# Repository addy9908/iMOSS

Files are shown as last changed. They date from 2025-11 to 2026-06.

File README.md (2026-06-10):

# <b>iMOSS</b>: Immobility/Mobility Optimized Scoring System
<p align="center">
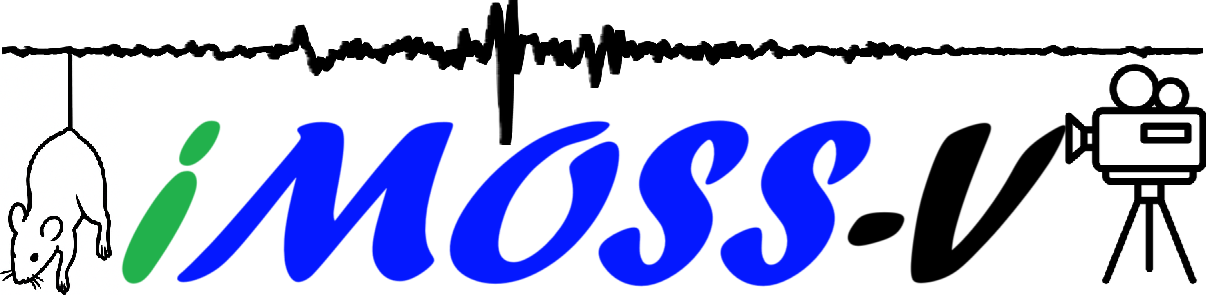
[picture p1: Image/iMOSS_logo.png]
iMOSS Logo
  
</p>   

<p align="center">
  <a href="https://www.frontiersin.org/journals/behavioral-neuroscience/articles/10.3389/fnbeh.2026.1819512/full">
    
  </a>
  
  
  
</p>

---

## 📌 Overview

**iMOSS** is an open-source platform for high-resolution immobility scoring in the tail suspension test (TST). By enabling precise synchronization with neural recordings, this platform supports critical advances in neuroscience and public health research.

### 🔑 Key Features
| Feature | Description |
|---|---|
| **iMOSS-MV** | Frame-accurate binary behavior manual scoring |
| **iMOSS-AS** | High-frequency automated scoring (80 Hz) |
| **Integration** | Seamless synchronization with neural recording systems |
| **Analysis** | Standardized and reproducible behavioral data processing |

---

## 🔄 Workflow

<p align="center">
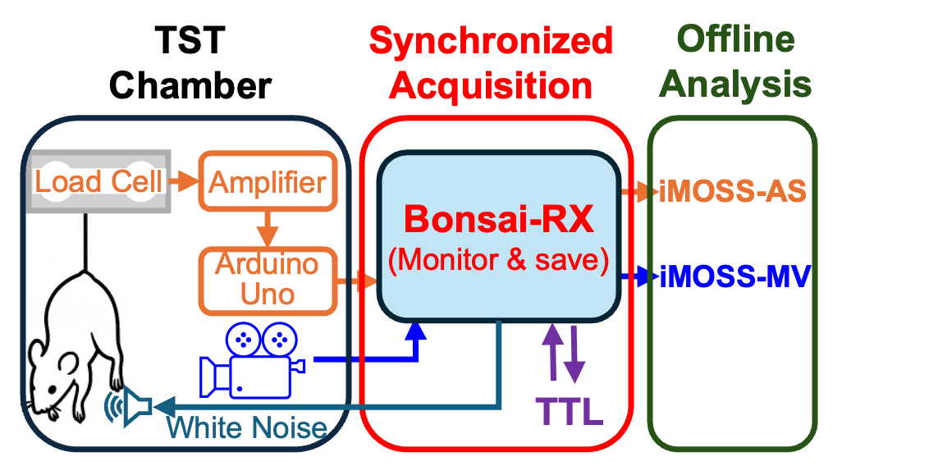
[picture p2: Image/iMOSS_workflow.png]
Detailed Workflow
  
</p>

---

## 🧰 Materials

<p align="center">
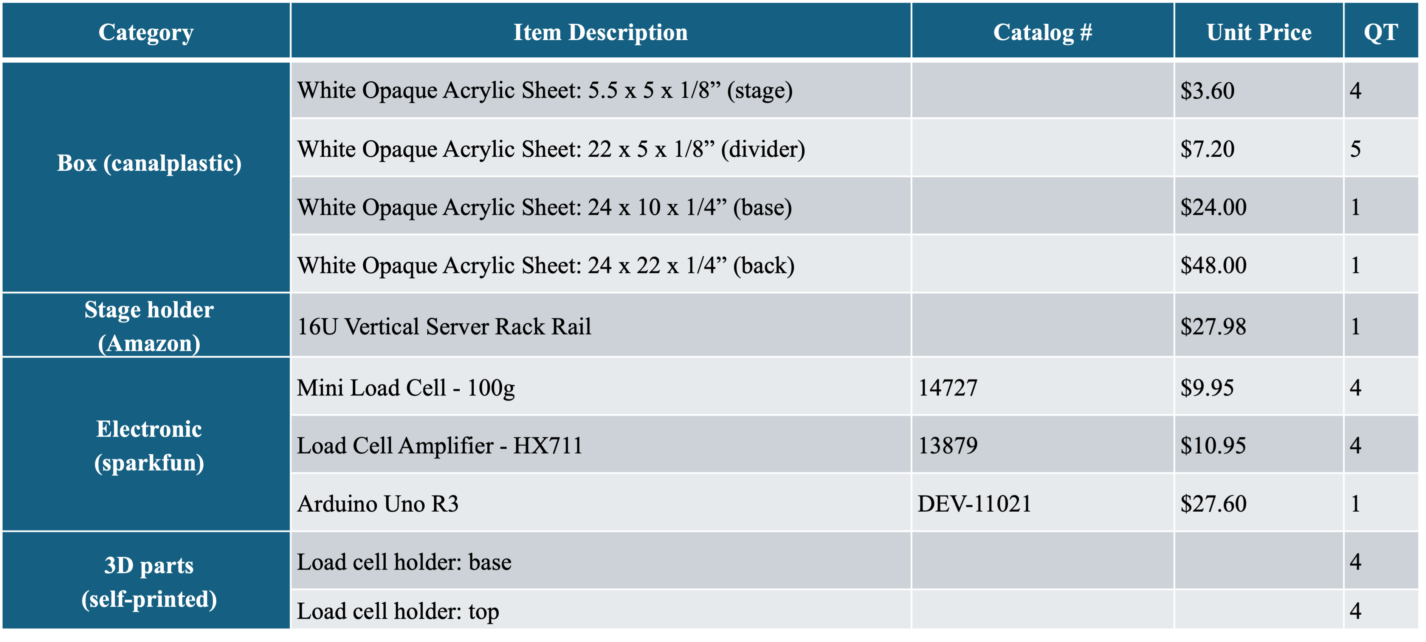
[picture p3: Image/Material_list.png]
Material List
  
</p>

---

## 🏗️ TST Chamber Design

<p align="center">
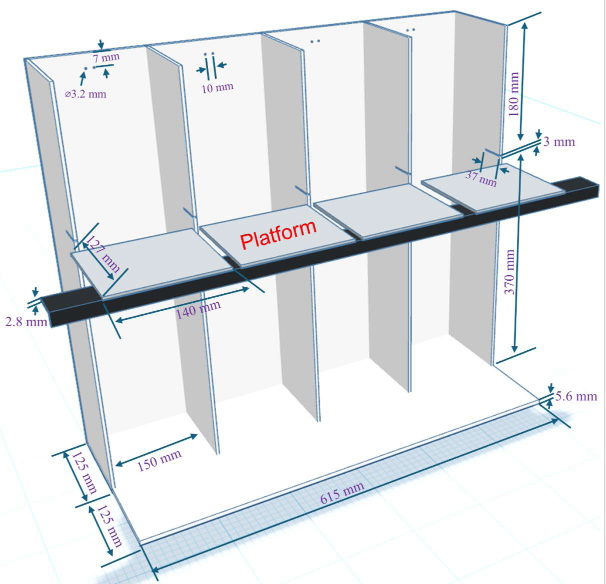
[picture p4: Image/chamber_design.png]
Chamber Design
	
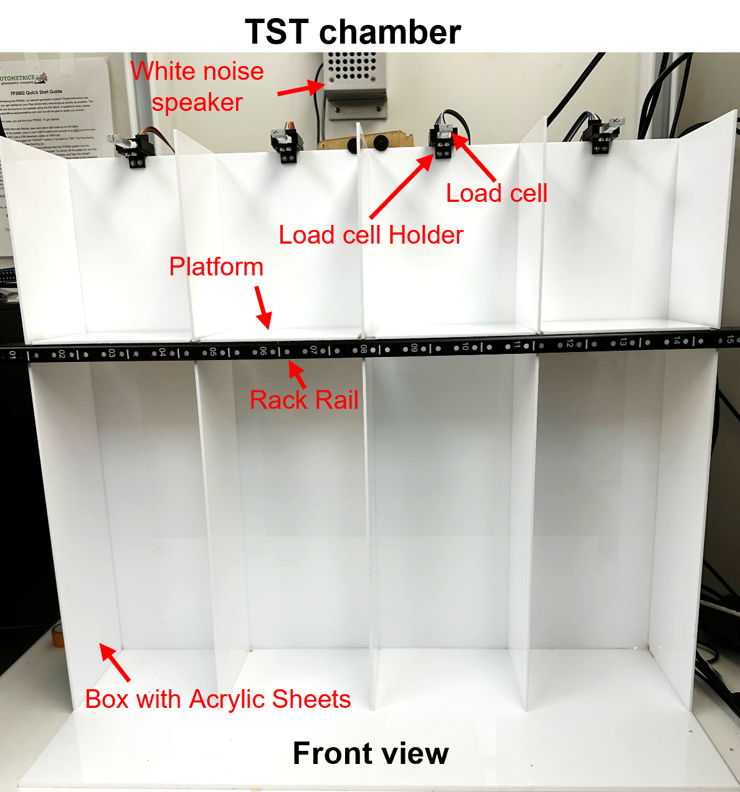
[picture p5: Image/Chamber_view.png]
Front View
	 
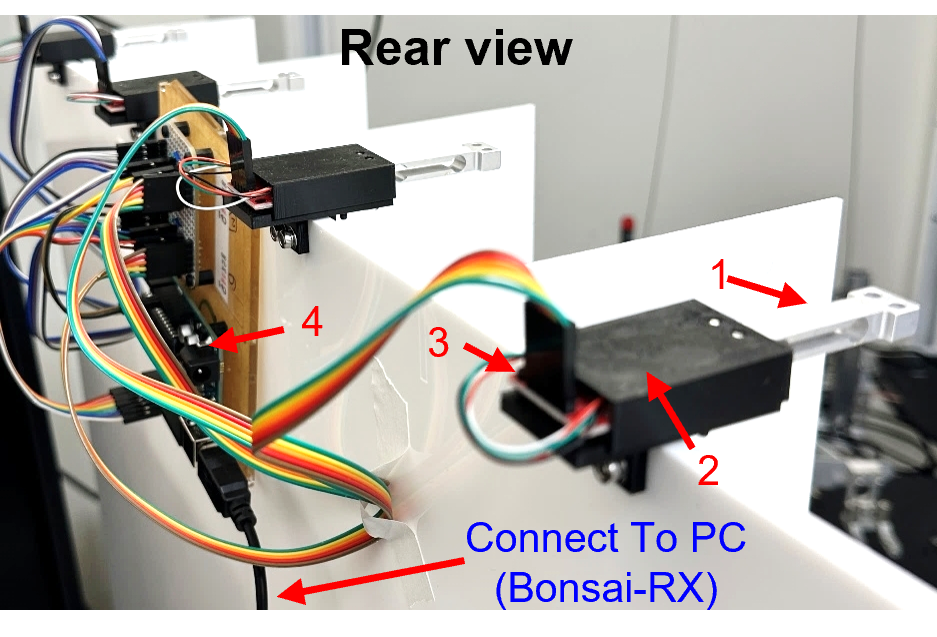
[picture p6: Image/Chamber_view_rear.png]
Rear View
	 
</p>

---

## ⚙️ iMOSS-AS Hardware Module

### 🔌 Design & Wiring

<p align="center">
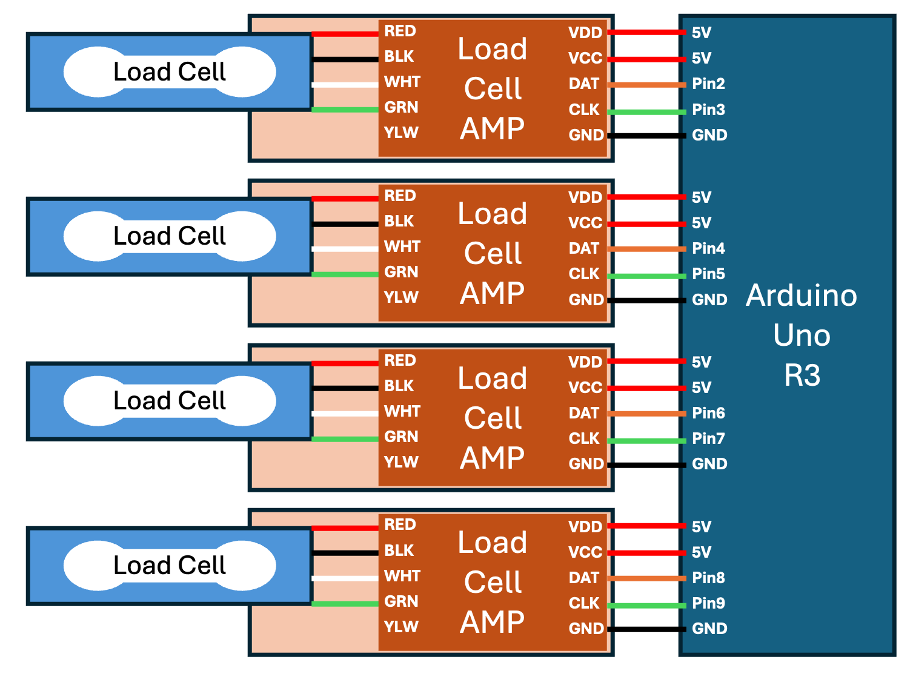
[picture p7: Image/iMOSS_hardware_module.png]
Hardware Wiring
  
</p>

### ⚠️ Important Note

To achieve the **80 Hz sampling rate**, the load cell amplifier must be modified as shown below:

<p align="center">
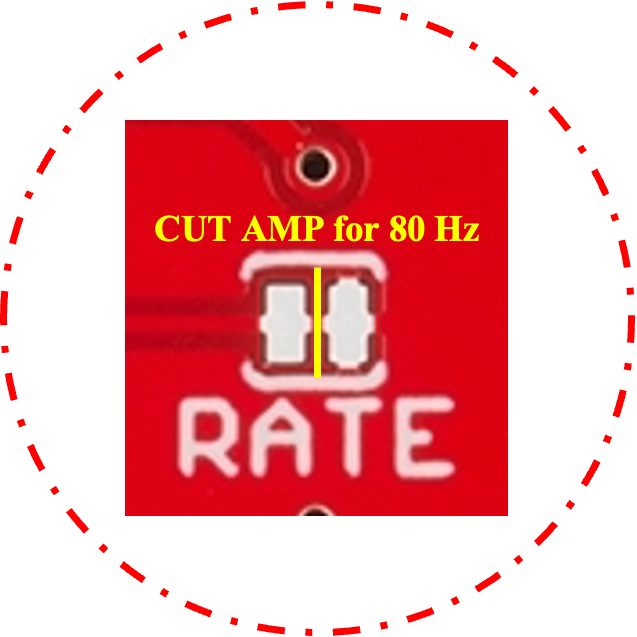
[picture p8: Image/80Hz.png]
Loadcell Amplifier Modification
  
</p>

---

## 🔌 Firmware (Arduino Uno)

### 📥 Download
The firmware file is available here: `Firmware/iMOSS_AS_V1.ino`  
[Direct Link to Firmware Folder](https://github.com/addy9908/iMOSS/tree/main/Firmware)

### 🚀 Flashing Instructions
1. Install **Arduino IDE**.
2. Connect your **Arduino Uno**.
3. Open `iMOSS_AS_V1.ino`.
4. Click **Upload**.

<details>
<summary>Click for Arduino Code Preview</summary>

```cpp
//-------------------------------------------------------------------------------------
// iMOSS-AS for automatic tail suspension test with 4 load cells
//Author: Zengyou Ye at NIDA/IRP
//Date: 10/23/2024

// Settling time (number of samples) and data filtering can be adjusted in the config.h file of HX711_ADC.h
// HX711-ADC from: https://github.com/olkal/HX711_ADC
//---------------------------------

#include <HX711_ADC.h>

//pins:
const int HX711_dout_1 = 2; //mcu > HX711 no 1 dout pin
const int HX711_sck_1 = 3; //mcu > HX711 no 1 sck pin
const int HX711_dout_2 = 4; //mcu > HX711 no 2 dout pin
const int HX711_sck_2 = 5; //mcu > HX711 no 2 sck pin
const int HX711_dout_3 = 6; //mcu > HX711 no 3 dout pin
const int HX711_sck_3 = 7; //mcu > HX711 no 3 sck pin
const int HX711_dout_4 = 8; //mcu > HX711 no 4 dout pin
const int HX711_sck_4 = 9; //mcu > HX711 no 4 sck pin

//HX711 constructor (dout pin, sck pin)
HX711_ADC LoadCell_1(HX711_dout_1, HX711_sck_1); //HX711 1
HX711_ADC LoadCell_2(HX711_dout_2, HX711_sck_2); //HX711 2
HX711_ADC LoadCell_3(HX711_dout_3, HX711_sck_3); //HX711 3
HX711_ADC LoadCell_4(HX711_dout_4, HX711_sck_4); //HX711 4

unsigned long t = 0;
const int serialPrintInterval = 12.5; //80Hz to match 80SPS
static boolean togo = 0;

void setup() {
  Serial.begin(57600);
  delay(10);
  Serial.println();
  Serial.println("Starting...");

  float calibrationValue_1; // calibration value load cell 1
  float calibrationValue_2; // calibration value load cell 2
  float calibrationValue_3; // calibration value load cell 3
  float calibrationValue_4; // calibration value load cell 4

  calibrationValue_1 = 13.3; // uncomment this if you want to set this value in the sketch
  calibrationValue_2 = 13.3; // uncomment this if you want to set this value in the sketch
  calibrationValue_3 = 13.3; // uncomment this if you want to set this value in the sketch
  calibrationValue_4 = 13.3; // uncomment this if you want to set this value in the sketch

  LoadCell_1.begin();
  LoadCell_2.begin();
  LoadCell_3.begin();
  LoadCell_4.begin();

  unsigned long stabilizingtime = 2000; // tare preciscion can be improved by adding a few seconds of stabilizing time
  boolean _tare = true; //set this to false if you don't want tare to be performed in the next step
  byte loadcell_1_rdy = 0;
  byte loadcell_2_rdy = 0;
  byte loadcell_3_rdy = 0;
  byte loadcell_4_rdy = 0;

  while ((loadcell_1_rdy + loadcell_2_rdy + loadcell_3_rdy + loadcell_4_rdy) < 4) { //run startup, stabilization and tare, both modules simultaniously
    if (!loadcell_1_rdy) loadcell_1_rdy = LoadCell_1.startMultiple(stabilizingtime, _tare);
    if (!loadcell_2_rdy) loadcell_2_rdy = LoadCell_2.startMultiple(stabilizingtime, _tare);
    if (!loadcell_3_rdy) loadcell_3_rdy = LoadCell_3.startMultiple(stabilizingtime, _tare);
    if (!loadcell_4_rdy) loadcell_4_rdy = LoadCell_4.startMultiple(stabilizingtime, _tare);
  }
  if (LoadCell_1.getTareTimeoutFlag()) {
    Serial.println("Timeout, check MCU>HX711 no.1 wiring and pin designations");
  }
  if (LoadCell_2.getTareTimeoutFlag()) {
    Serial.println("Timeout, check MCU>HX711 no.2 wiring and pin designations");
  }
  if (LoadCell_3.getTareTimeoutFlag()) {
    Serial.println("Timeout, check MCU>HX711 no.3 wiring and pin designations");
  }
  if (LoadCell_4.getTareTimeoutFlag()) {
    Serial.println("Timeout, check MCU>HX711 no.4 wiring and pin designations");
  }
  LoadCell_1.setCalFactor(calibrationValue_1); // user set calibration value (float)
  LoadCell_2.setCalFactor(calibrationValue_2); // user set calibration value (float)
  LoadCell_3.setCalFactor(calibrationValue_3); // user set calibration value (float)
  LoadCell_4.setCalFactor(calibrationValue_4); // user set calibration value (float)
  Serial.print("HX711 measured sampling rate Hz: ");
  Serial.println(LoadCell_1.getSPS());
  Serial.println("Startup is complete");
}

void loop() {
  while (togo==0){
    char inByte = Serial.read();
    if (inByte == 'g') {
      togo=1;
      //Serial.println("ms,lc1,lc2,lc3,lc4");
      //Serial.println("experiments on");
    }
    if (inByte == 't') {
      LoadCell_1.tareNoDelay();
      LoadCell_2.tareNoDelay();
      LoadCell_3.tareNoDelay();
      LoadCell_4.tareNoDelay();
      delay(5000);
    }    
  }
  if(togo){
    LoadCell_1.update();
    LoadCell_2.update();
    LoadCell_3.update();
    LoadCell_4.update();

    if (millis() >= t + serialPrintInterval) {
      t = millis();
      float a = LoadCell_1.getData();
      float b = LoadCell_2.getData();
      float c = LoadCell_3.getData();
      float d = LoadCell_4.getData();
      
      Serial.print(t);
      Serial.print(",");
      Serial.print(a);
      Serial.print(",");
      Serial.print(b);
      Serial.print(",");
      Serial.print(c);
      Serial.print(",");
      Serial.println(d);
    }
  }
  if (Serial.read() == 'q') {
    togo=0;
  }
}
```
</details>

---

## 📡 Data Acquisition (Bonsai-RX)

### 📥 Workflow File
`Bonsai/ZY_tailSuspension_V11_Opstim.bonsai`
`Bonsai/ZY_TST_FP.bonsai`

### 💻 Workflow Layout and UI from V11
<p align="center"> 
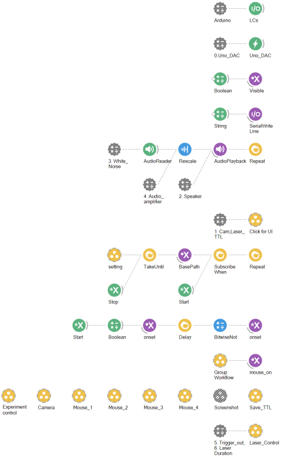
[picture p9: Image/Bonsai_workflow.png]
Bonsai Layout
	
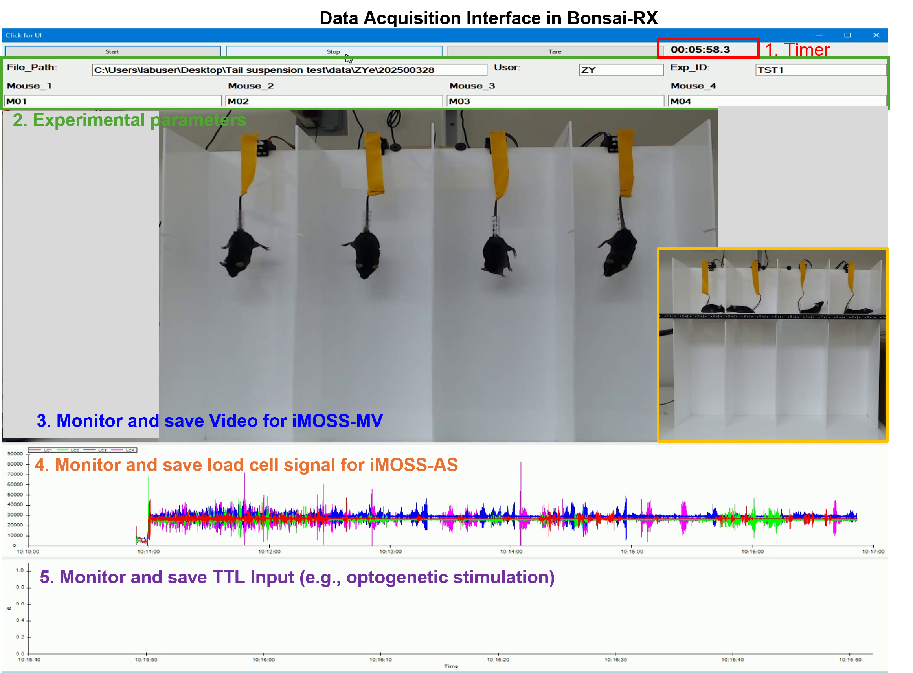
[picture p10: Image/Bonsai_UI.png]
Bonsai UI
	
</p>

---

## 🧪 Data Analysis

### Python Envirement Installation:
  1. Install Anaconda
  2. Importing the listed "[yaml](Data_Analysis/)" environment file 
  3. Install Spyder in this environment
  4. Download Main script as well as Required script in the same folder
  4. Run Main Script inside Spyder.
---
### 🖥️ iMOSS-MV (Manual Scoring)
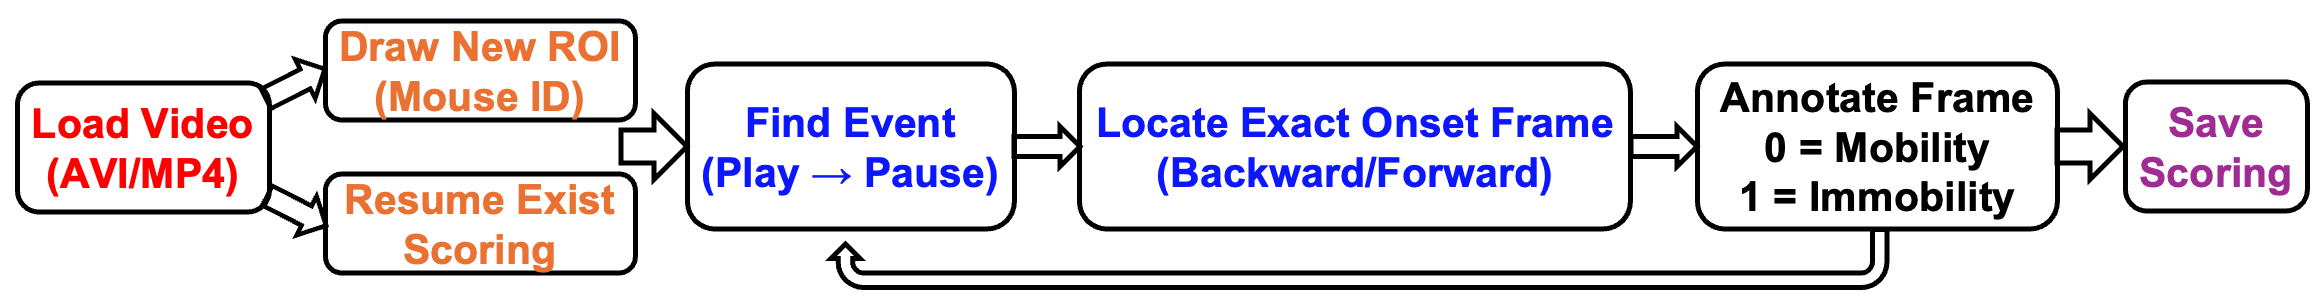
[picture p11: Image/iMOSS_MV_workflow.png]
iMOSS-MV Workflow


#### 📦 Requirements
| Main Script | Conda Env | Link to Folder | Spyder Version |
|---|---|---|---|
| zy_iMOSS_MV_20251119.py | video_scorer.yaml | [iMOSS-MV V1](Data_analysis/iMOSS_MV/V1) | 6.05 |
| zy_iMOSS_MV_withDuration.py | video_scorer.yaml | [iMOSS-MV V2](Data_analysis/iMOSS_MV/V2) | 6.05 |
| zy_iMOSS_MV_20260501.py | iMOSS_MV_20260501.yml | [iMOSS-MV V3](Data_analysis/iMOSS_MV/V3) | 6.13 |

<p align="center"> iMOSS MV V1
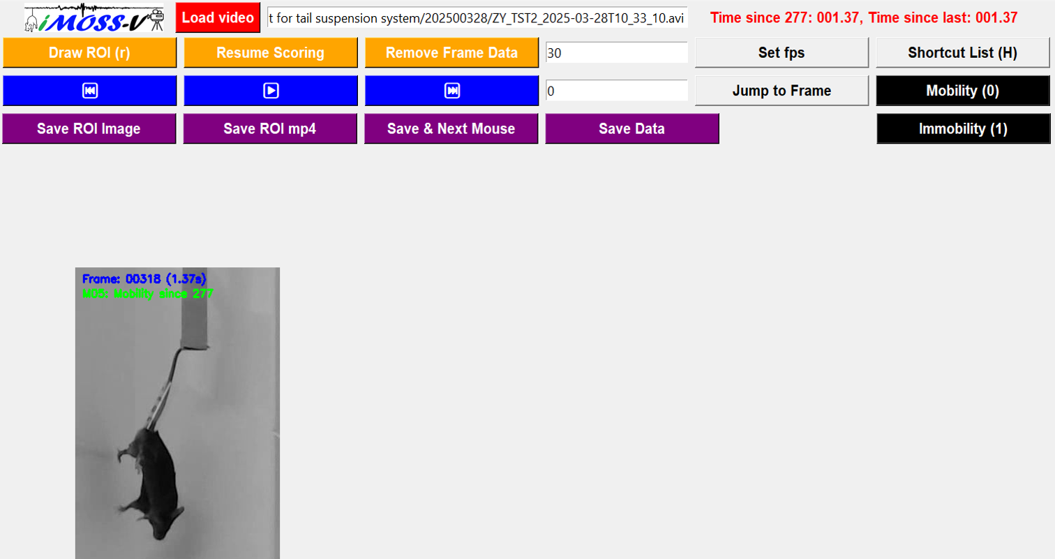
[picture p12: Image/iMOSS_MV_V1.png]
iMOSS MV V1
	
</p>
<p align="center"> iMOSS MV V3
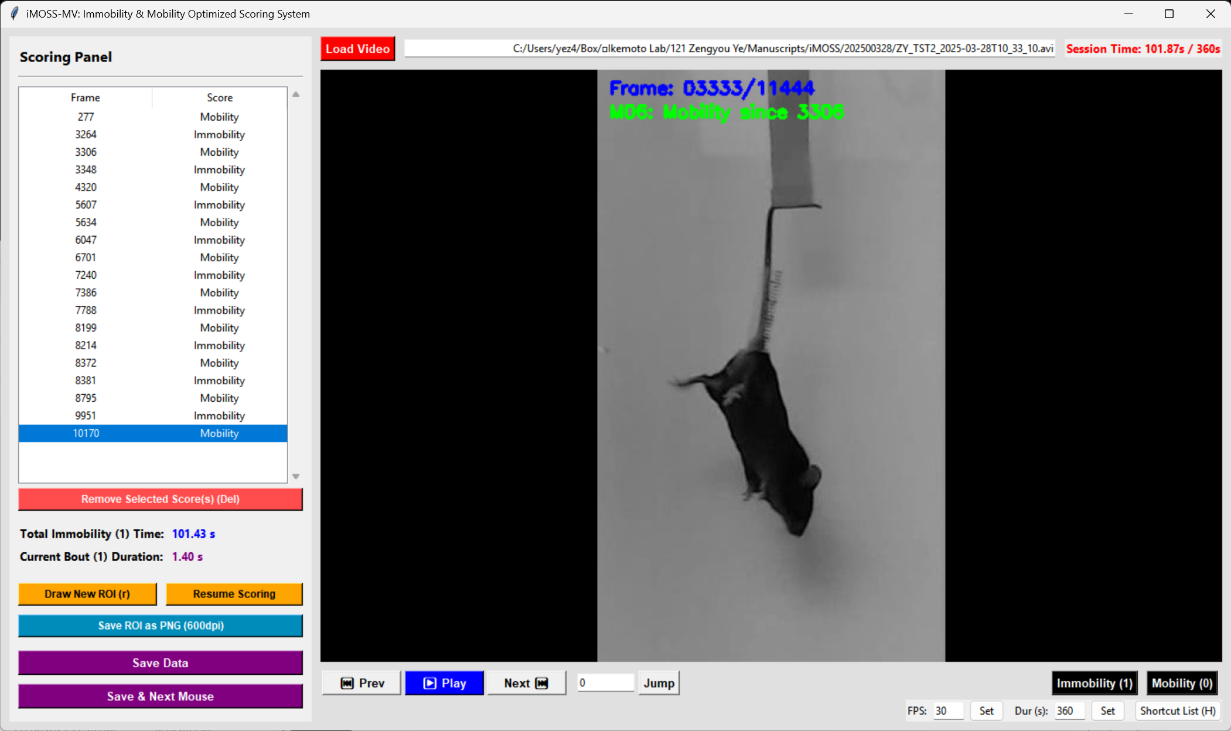
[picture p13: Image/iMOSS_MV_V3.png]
iMOSS MV V3
	
</p>

### Scoring with iMOSS-MV (zy_iMOSS_MV_20251119.py):
  1. Load video file
  2. Draw ROI, and comforn the ROI with SPACE or ENTER key, then define Mouse_ID
  3. Use Buttons or keyboard shrcuts (detailed in "shortcuts" bottun) to navigate the video and mark the events.
  4. When finish annotating a ROI, click "Save Data" to save the ROI information (csv file) and immobility data (excel file)
  5. Optional:
     1. click "Save & Next Mouse" will also save the data and promp user to choose next ROI
     2. click "Draw ROI (r)" will also prompt user to save the data if exist.

⚠️ update: 
* [**V2**](Data_Analysis/iMOSS_MV/V2): allow user to set the duration of session and adjust the size of video for other purposes.
* [**V3**](Data_Analysis/iMOSS_MV/V2): new design with better layout, and improve the Compatibility with new opencv  
---

### 🤖 iMOSS-AS (Automated Scoring)

<p align="center"> iMOSS-AS Workflow </p>

#### 📦 Requirements
| Main Script | Required Script | Conda Env | Folder | Spyder Version |
|---|---|---|---|---|
| zy_iMOSS_AS_20251119_clean.py| zy_importer_lite_V4.py; zy_preset_mpl_v2.py | zy_NIDA_20240905.yaml | [iMOSS-AS V1](Data_analysis/iMOSS_AS/Archive_V1) | 6.05 |
| zy_iMOSS_AS_20260501_with_summary.py | zy_importer_lite_V5.py; zy_preset_mpl_v2.py | iMOSS_AS.yml| [iMOSS-AS V2](Data_analysis/iMOSS_AS/V2) | 6.13 |

---

## 📄 Publication

For detailed scientific methodology, validation, and synchronization with Fiber Photometric recording, please refer to our paper:  
[Frontiers in Behavioral Neuroscience (2026)](https://www.frontiersin.org/journals/behavioral-neuroscience/articles/10.3389/fnbeh.2026.1819512/full)

---

## 📚 Citation

```bibtex
@article{iMOSS2026,
  title={iMOSS: an integrated open-source tail suspension test platform for high-resolution immobility scoring and synchronization with neural activity},
  journal={Frontiers in Behavioral Neuroscience},
  year={2026},
  doi={10.3389/fnbeh.2026.1819512}
}
```

---

## 🤝 Contributions

We welcome feedback and contributions from the community. If you find this platform helpful for your research, please ⭐ the repository.

## This iMOSS platform is under a MIT license.

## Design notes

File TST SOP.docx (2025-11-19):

Tail Suspension Test Standard Operating Protocol

Zengyou Ye at Ikemoto Lab, NIDA

1. Open Bonsai:
  - Select the appropriate program: ZY_tailSuspension_V8_Opstim.
2. Confirm Hardware Selections in Bonsai:
  - Verify the Arduino Uno port, camera, and speaker settings on the right panel.
3. Optional - Optogenetic Stimulation Setup:
  a. Power on the Doric "Laser Diode Fiber Light Source" and launch the corresponding software.
  b. Within the software, connect the "Laser Diode Fiber Light Source".
  c. Load an existing configuration or create a new one (gate control with restart option is recommended).
  d. Confirm the current output and start the setup, then leave it running.
4. Run Bonsai File:
  - This will initiate white noise playback and display a User Interface (UI). If the UI does not appear automatically, click the "Click for UI" node.
5. Set Parameters in UI:
  - Enter the file path, User ID, Experimental ID, and Mouse ID in the UI.
6. Start the Test:
  a. Click the "Start" button.
  b. Place the mice onto the stage of the Tail Suspension Test (TST) box.
  c. For Optogenetic Stimulation: Place the mice first, connect the fiber patch cable to the cannulas, then click "Start"
7. Begin Recording:
  - Remove the stage from the TST box to initiate recording and monitor the timer on the UI.
8. End Recording:
  - After 6 minutes, replace the stage in the TST box and click the "Stop" button.
9. Remove Mice:
  - Take the mice off the stage.
10. Repeat for Additional Mice:
  - Repeat steps 5-9 for the next set of mice.

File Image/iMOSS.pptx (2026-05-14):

## Hardware of iMOSS

Zengyou Ye
https://www.github.com/addy9908/iMOSS
Updated on 05/13/2026

## iMOSS workflow

TST
Chamber

White Noise

Synchronized
Acquisition

Bonsai-RX
(Monitor & save)

Offline
Analysis

iMOSS-AS

iMOSS-MV

Load Cell

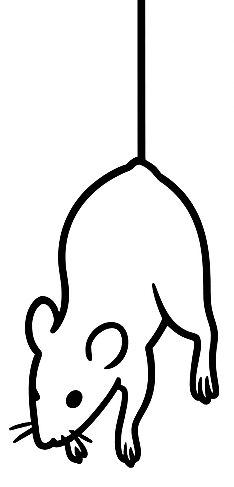
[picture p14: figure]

Amplifier

Arduino Uno

TTL

## Material list

Category | Item Description | Catalog # | Unit Price | QT
Box (canalplastic) | White Opaque Acrylic Sheet: 5.5 x 5 x 1/8” (stage) | | $3.60 | 4
| White Opaque Acrylic Sheet: 22 x 5 x 1/8” (divider) | | $7.20 | 5
| White Opaque Acrylic Sheet: 24 x 10 x 1/4” (base) | | $24.00 | 1
| White Opaque Acrylic Sheet: 24 x 22 x 1/4” (back) | | $48.00 | 1
Stage holder (Amazon) | 16U Vertical Server Rack Rail | | $27.98 | 1
Electronic (sparkfun) | Mini Load Cell - 100g | 14727 | $9.95 | 4
| Load Cell Amplifier - HX711 | 13879 | $10.95 | 4
| Arduino Uno R3 | DEV-11021 | $27.60 | 1
3D parts (self-printed) | Load cell holder: base | | | 4
| Load cell holder: top | | | 4

## iMOSS-AS hardware module

Load Cell

Load
Cell
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
Pin2

Pin3

GND

Load Cell

Load
Cell
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
Pin4

Pin5

GND

Load Cell

Load
Cell
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
Pin6

Pin7

GND

Load Cell

Load
Cell
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
Pin8

Pin9

GND

Arduino
Uno
R3

CUT AMP for 80 Hz

Note: To archive 80Hz sampling rate, we need to cut the back of load cell amplifier

## Bonsai workflow

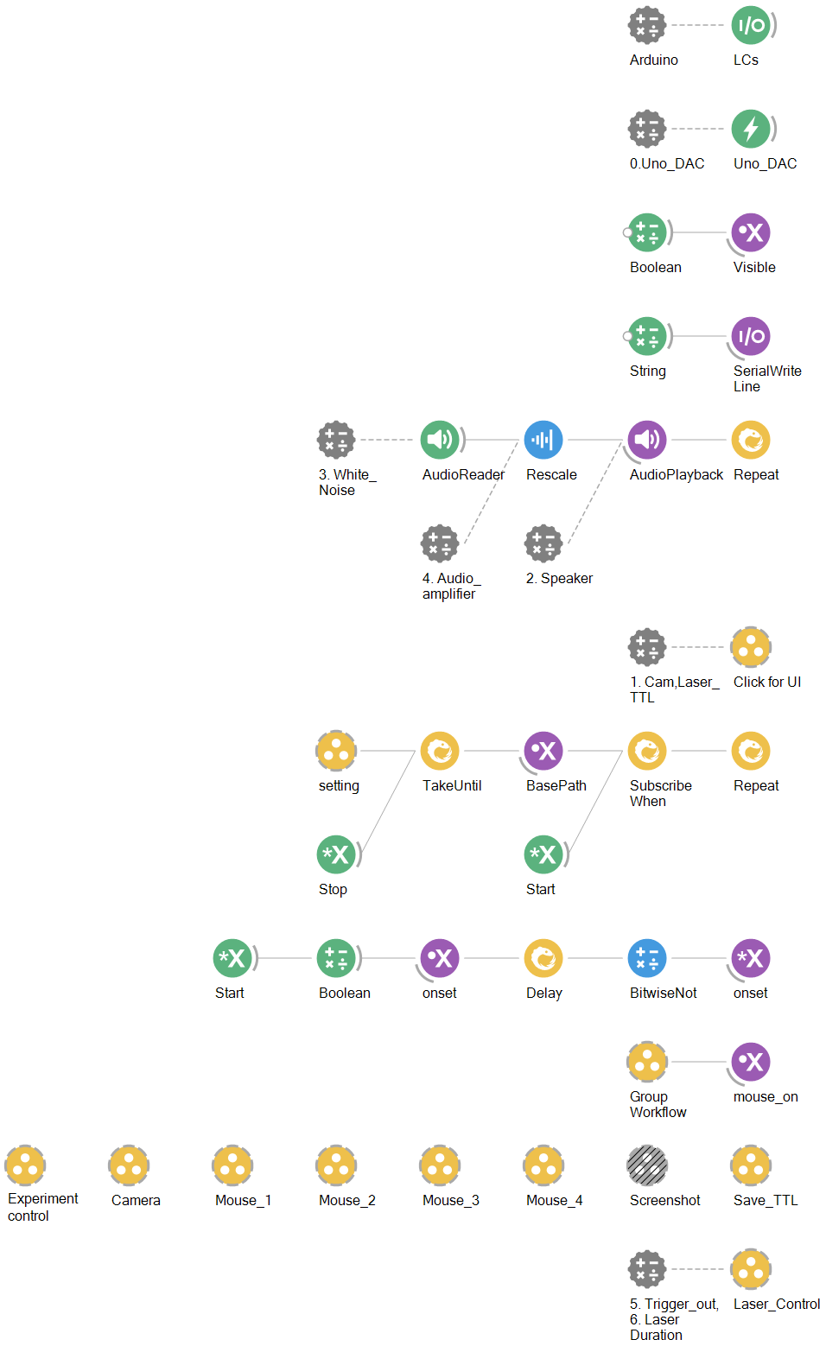
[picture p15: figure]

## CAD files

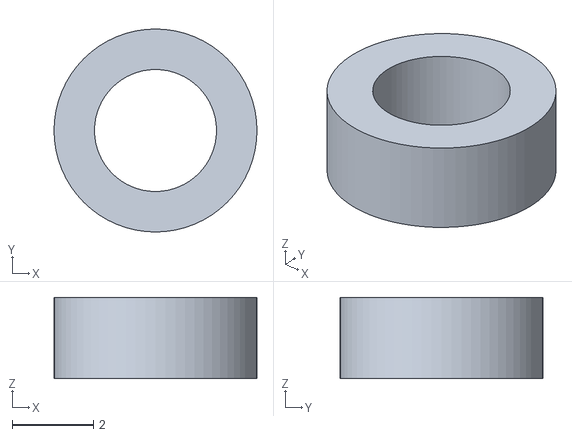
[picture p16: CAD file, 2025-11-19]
3D_parts/load cell holder_spacer.stl
5.00 x 5.00 x 2.00

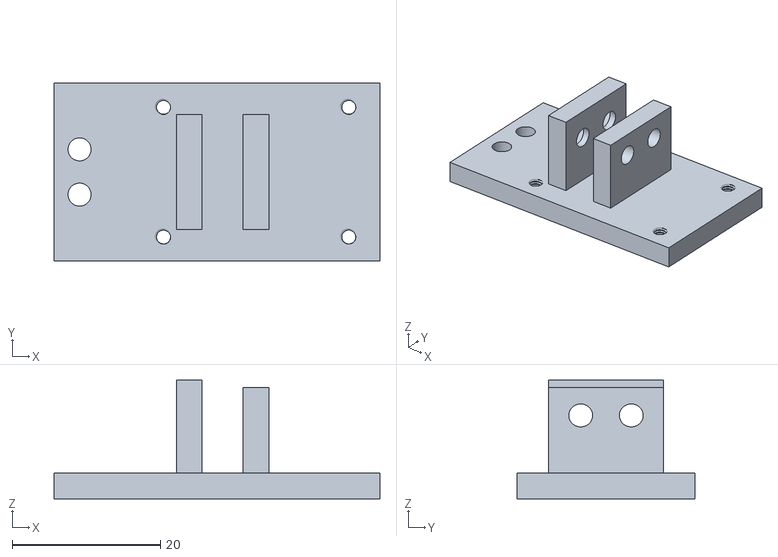
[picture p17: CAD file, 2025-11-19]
3D_parts/load cell holder_base.stl
44.0 x 24.0 x 16.0

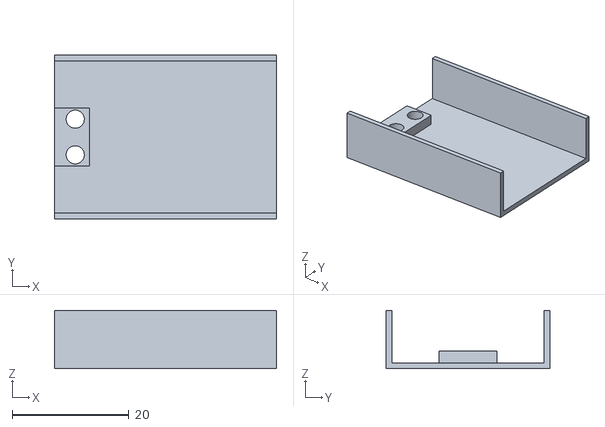
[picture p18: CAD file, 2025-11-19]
3D_parts/load cell holder_top.stl
38.0 x 28.0 x 10.0

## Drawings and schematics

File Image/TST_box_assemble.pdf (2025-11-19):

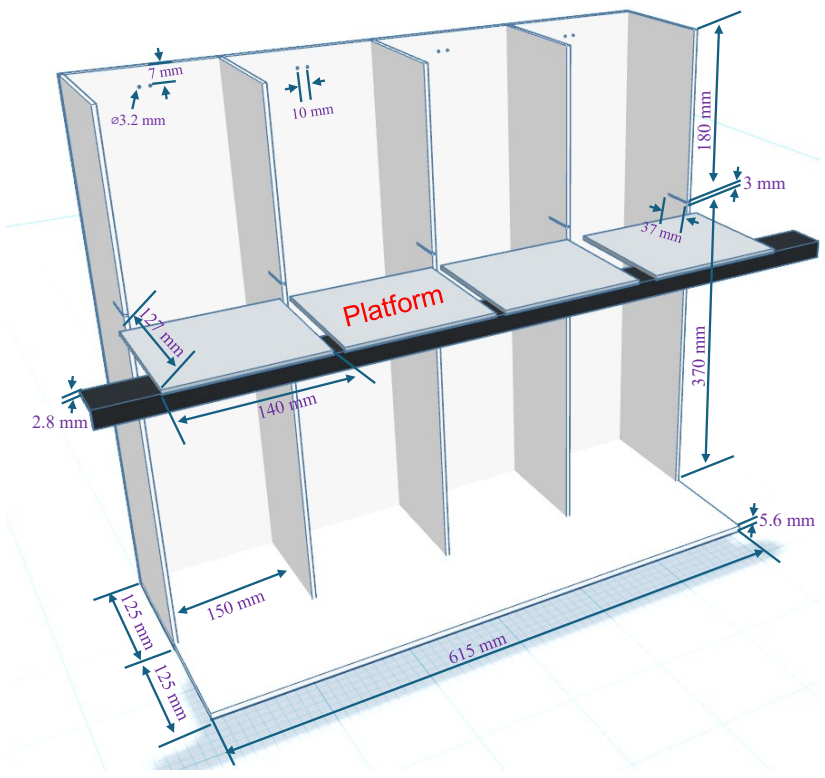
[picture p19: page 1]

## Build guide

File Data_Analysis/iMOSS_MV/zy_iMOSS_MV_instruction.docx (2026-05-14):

Instruction Manual for iMOSS-MV V1

Purpose

The Video Frame Labeler is a user-friendly, open-source software designed to manually score mobility and immobility (or other binary behaviors) in behavioral experiments such as the Tail Suspension Test (TST) and Forced Swim Test (FST). Researchers can efficiently annotate video frames, categorizing behavior as either mobility or immobility while maintaining precise frame control.

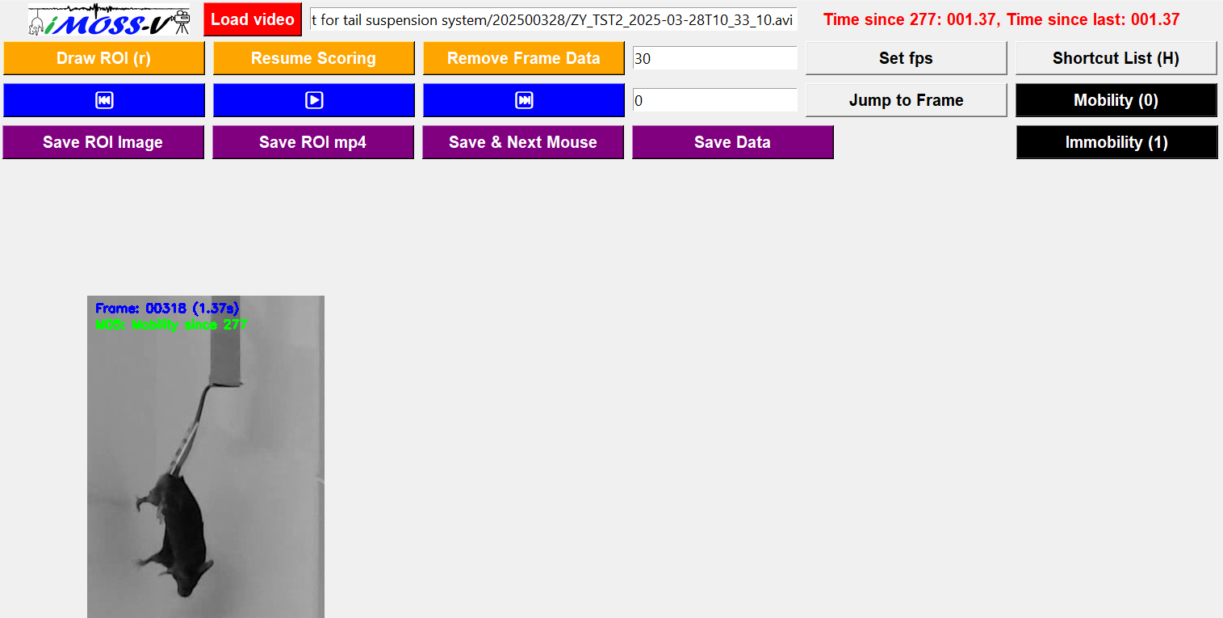
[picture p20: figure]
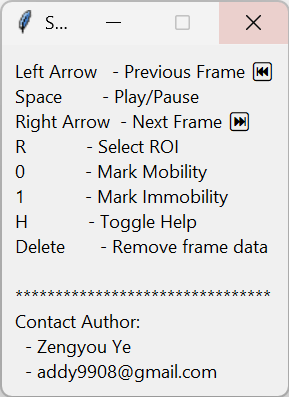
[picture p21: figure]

Key Features & Advantages

- Flexible Interaction: Supports both button clicks and keyboard shortcuts for efficient scoring.
- Precise Frame Control: Easily play, pause, move forward, or rewind frame-by-frame for accurate annotation.
- Region of Interest (ROI) Selection: Define and save ROIs for individual subjects, ensuring consistent tracking across frames.
- Data Management:
  - Save annotations as CSV files for easy analysis.
  - Reload previously annotated data for continued analysis or presentation.
  - Prevent accidental overwrites with smart saving mechanisms.
- Real-Time Time Display: Converts frame numbers into MM:SS.SS format for easier interpretation.
- Open-Source & Budget-Friendly: Designed for labs with limited resources, making video scoring accessible without expensive commercial software.

How to Use

1. Load a Video File

- Click Browse to select a video file (AVI format preferred).
- Click Load Video to open and process the video.

2. Select Region of Interest (ROI)

- Click Select ROI, and a pop-up window will appear.
- Define an ROI by dragging a box over the desired area, then confirm with Space or Enter.
- Assign a Mouse ID to track the subject.
- The ROI will be saved and displayed on the canvas.

3. Play & Navigate the Video

- Play/Pause: Use the button or press Space.
- Move Forward/Backward: Click buttons or use Right/Left Arrow Keys.
- Jump to Specific Frame: Enter a frame number manually.

4. Annotate Behavior

- Press 0 for Mobility.
- Press 1 for Immobility.
- Annotations will be saved automatically per frame.

5. Save & Reload Data

- Click Save to export the scored data (CSV format, timestamped filename).
- When reloading a video, existing ROIs will be detected, and a warning will prompt confirmation before clearing them.
- Previously saved data can be reloaded for continued analysis.

Additional Notes

- ROIs are preserved per session unless cleared manually.
- Ensure consistent FPS settings for accurate frame-time conversion.
- Data integrity is maintained with built-in duplicate checks when saving.

This tool simplifies manual behavioral scoring, ensuring flexibility, precision, and ease of use for researchers conducting stress behavior studies.

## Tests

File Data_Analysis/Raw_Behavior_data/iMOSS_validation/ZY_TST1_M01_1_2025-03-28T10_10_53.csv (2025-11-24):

TimeStamp | Millis | Loadcell
2025-03-28T10:10:53.9370880-04:00 | 36653937.088 | 19262.93
2025-03-28T10:10:53.9403776-04:00 | 36653940.377599999 | 15551.799999999999
2025-03-28T10:10:53.9405952-04:00 | 36653940.595200002 | 11794.129999999999
2025-03-28T10:10:53.9407872-04:00 | 36653940.787200004 | 7884.6599999999999
2025-03-28T10:10:53.9409792-04:00 | 36653940.979199998 | 7886.54
2025-03-28T10:10:53.9411712-04:00 | 36653941.1712 | 7886.3900000000003
2025-03-28T10:10:53.9516928-04:00 | 36653951.6928 | 7886.6899999999996
2025-03-28T10:10:53.9640192-04:00 | 36653964.019200005 | 7866.0100000000002
2025-03-28T10:10:53.9763456-04:00 | 36653976.345600002 | 7851.1300000000001
2025-03-28T10:10:53.9886080-04:00 | 36653988.608000003 | 7855.9399999999996
2025-03-28T10:10:54.0008320-04:00 | 36654000.832000002 | 7862.0299999999997
2025-03-28T10:10:54.0130304-04:00 | 36654013.030400001 | 7873.5299999999997
2025-03-28T10:10:54.0253440-04:00 | 36654025.344000004 | 7891.7299999999996
2025-03-28T10:10:54.0376576-04:00 | 36654037.657600001 | 7898.1999999999998
2025-03-28T10:10:54.0499456-04:00 | 36654049.945600003 | 7896.9200000000001
2025-03-28T10:10:54.0622592-04:00 | 36654062.259199999 | 7893.46
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

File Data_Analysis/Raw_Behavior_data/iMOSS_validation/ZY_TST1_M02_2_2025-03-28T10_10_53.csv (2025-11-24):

TimeStamp | Millis | Loadcell
2025-03-28T10:10:53.9392128-04:00 | 36653939.212800004 | 2303.0100000000002
2025-03-28T10:10:53.9403904-04:00 | 36653940.3904 | 4669.0200000000004
2025-03-28T10:10:53.9405952-04:00 | 36653940.595200002 | 6956.6199999999999
2025-03-28T10:10:53.9408000-04:00 | 36653940.800000004 | 9241.2800000000007
2025-03-28T10:10:53.9409920-04:00 | 36653940.991999999 | 9071.7299999999996
2025-03-28T10:10:53.9411712-04:00 | 36653941.1712 | 8902.8600000000006
2025-03-28T10:10:53.9517184-04:00 | 36653951.718400002 | 8805.8600000000006
2025-03-28T10:10:53.9640448-04:00 | 36653964.044799998 | 8766.6900000000005
2025-03-28T10:10:53.9763712-04:00 | 36653976.371200003 | 8818.0400000000009
2025-03-28T10:10:53.9886336-04:00 | 36653988.633600004 | 8696.3899999999994
2025-03-28T10:10:54.0008704-04:00 | 36654000.870400004 | 8438.7999999999993
2025-03-28T10:10:54.0130432-04:00 | 36654013.043200001 | 8115.1099999999997
2025-03-28T10:10:54.0253696-04:00 | 36654025.369600005 | 7594.4399999999996
2025-03-28T10:10:54.0376832-04:00 | 36654037.683200002 | 6780.3800000000001
2025-03-28T10:10:54.0499840-04:00 | 36654049.984000005 | 6546.54
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

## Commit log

2025-11-19 create iMOSS for publication
    [load cell holder_base.stl, load cell holder_spacer.stl, load cell holder_top.stl]
2025-11-21 Update zy_iMOSS_MV_20251119.py
    add absFrameTime starting from 1st Frame
2025-11-24 raw data
    [ZY_FP1_FP_2025-06-24T10_13_41.csv, ZY_FP1_M10_2_2025-06-24T10_13_41.csv, ZY_FP1_M11_4_2025-06-24T10_13_41.csv, ZY_FP1_cam_2025-06-24T10_13_42.csv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]
2026-05-01 Update to iMOSS-AS code
    I have rewritten the code as 20260501, including zy_importer_lite_V5, to improve compatibility with newer versions of Spyder (resolving Tk-related issues).
    An additional update introduces an all-in-one summary CSV export that compiles results from all processed batch files.
    If you do not need to save figures or generate the more complex Excel database, you can uncheck “save files” to reduce runtime and storage usage.
